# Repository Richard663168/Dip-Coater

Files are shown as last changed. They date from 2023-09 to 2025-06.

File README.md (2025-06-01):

# Dip-Coater
**Design of an Inexpensive, Microcontroller-based Dip Coater for Automated Thin Film Deposition**  

<p align="center">  
dipcoater  
  
**Animated Dip Coater Assembly Video**: https://youtu.be/RGj2P8bEvw4?si=eDrItM7gs5JFvn3  

Sections in this README:  

[1. Materials](#materials)

[2. 3D Printing Instructions](#3d-printing-instructions)

[3. Laser Cutting Instructions](#laser-cutting-instructions)  

[4. Circuit Design](#circuit-design)  

[5. Assembly Instructions](#assembly-instructions)  

[6. Using the Dip Coater](#using-the-dip-coater)  

## Materials  
Links provided below are only for reference.  

**Main Components**
| Item | Quantity | Reference Price | Source |
| ----------------------- | --------------- |---------------- |---------------- |
| [Arduino Mega 2560](https://www.amazon.com/ARDUINO-MEGA-2560-REV3-A000067/dp/B0046AMGW0)| 1  | $20.99 for 1|Amazon |
| ST7789 2.4” SPI LCD | 1  | $6.99 for 1| Taobao|
| [Nema 17 Stepper Motor](https://www.amazon.com/dp/B07THK76QQ/ref=twister_B07ZVLYL25?_encoding=UTF8&psc=1)  |1  | $10.99 for 1|Amazon|
| [2.1x5.5 12V Power Barrel](https://www.mcmaster.com/8320N117)  | 1 | $1.24 for 1|McMaster-Carr|
|[ DM542T Stepper Motor Driver  ](https://www.amazon.com/dp/B06Y5VPSFN?psc=1&ref=ppx_yo2ov_dt_b_product_details)| 1 | $28.99 for 1|Amazon|
| [DM320T Stepper Motor Driver](https://www.amazon.com/gp/product/B075R88FMN/ref=ppx_yo_dt_b_search_asin_title?ie=UTF8&psc=1)  |  1 | $15.99 for 1 |Amazon |
| [3x4 Matrix Keypad](https://www.adafruit.com/product/3845) |  1 | $6.50 for 1 |Adafruit Industries |
| [Screw Terminal Block Breakout Module for Arduino Mega](https://a.co/d/3ki64ex)  |  1 | $32.00 for 1 |Amazon |
| [FUYU FSL30 Mini Linear Stage Small Slide](https://a.co/d/0F66fWm)  |  1 | $118.00 for 1 |Amazon |
| [8-channel Bi-directional Logic Level Converter](https://www.adafruit.com/product/395?gclid=EAIaIQobChMIy_Wgl5aa-wIVg4zICh11Gg8HEAAYASAAEgIM5PD_BwE)|  1 | $7.95 for 1 |Adafruit Industries |
| [12V Push Button](https://www.amazon.com/gp/product/B08ZN73P2N/ref=ppx_yo_dt_b_search_asin_title?ie=UTF8&psc=1)  |  1 | $15.99 for 10 |Amazon |  
| [1 inch OD Steel Disk](https://a.co/d/e3l3wQv)  |  1 | $18.99 for 50 |Amazon |  
| [1/2 inch OD Steel Disk](https://a.co/d/1EjGdAq)  |  1 | $16.99 for 80 |Amazon |  
| [1 inch OD Neodymium magnet](https://www.mcmaster.com/7048T63)  |  1 | $8.57 for 1 |McMaster-Carr |  
| [1/2 inch OD Neodymium magnet](https://www.mcmaster.com/7048T56)  |  1 | $4.89 for 1 |McMaster-Carr |  

**Other Materials**
* 4 6mm 12" x 24" black acrylic sheets
* Wires
* Super glue
* 1 USB cable
* 1 2.1 x 5.5 12V power cable
* L-shape screw brackets
* Screws
* Clips
  
Black acrylic sheets could be replaced by other 6mm-thick laser cuttable materials.
## 3D Printing Instructions
3D printing files: Complete files are included in this current repository including .stl file format to be directly printable after slicing and .step file format to allow easy import and manipulation in most CAD software. All models were designed using Autodesk Fusion 360.

Designs are printed out using the Stratasys Elite and Stratasys Mojo with a layer height of 0.178mm (0.007in) and ABS plus P430 as the printing material.   

<details>

<summary>Printing Parts</summary>

* Beaker Disk
* Substrate Holder Connector
* Nema 17 Motor Holder
* Substrate Holder
* Disk Holder
* Tube Disk (Optional)
Asset 2@12x

</details>

## Laser Cutting Instructions
Laser Cutting files: Complete files are included in this current repository including .ai file format and .svg file format. All models were designed using Adobe Illustrator. Designs are laser cut using Epilog mini and Epilog Fusion with 6mm 12"x24" black acrylic sheets.  

The labels on the designs are for illustration only. It is recommanded to delete those labels before laser cutting or the labels might be engraved onto the final product. For Epilog laser cutters, the widths of the lines for laser cutting need to be set to 0.001pt and the area for engraving need to be filled black.

## Circuit Design

<p align="center">  
dipcoater_ciruit  
  
Breadboards shown in the circuit diagram are not required. It is recommanded to use solder or heat shrinking tubes to connect wires to electronic components and other wires in order to secure the connections.

## Assembly Instructions  
The **Complete Dip Coater** CAD file could be used as a reference on how to assemble the dip coater.  
1. Glue board **#3** and board **#2** onto board **#1**; Note that the back of the three pieces should not align: there is a 6mm distance between the back of board **#1** and the backs of both boards **#2** and **#3**
<p align="center">  
  

2. Use sandpaper or other sanding tools to make the edge of board **#4** fit the base and screw in the **ST7789 2.4” SPI LCD**, 2 **12V push buttons**, and the **3 x 4 keypad**
3. Glue board **#4** onto the dip coater
<p align="center">  


4.  Glue **Nema 17 Holder** onto the dip coater and place the **Nema 17 motor** inside
<p align="center">  


5. Glue boards **#5**, **#6**, and **#7** onto dip coater
<p align="center">  


6. Glue board **#8** onto the dip coater
<p align="center">  


7. Mount **FUYU FSL30 Mini Linear Stage Small Slide** onto board **#8** using screws
<p align="center">  


8. Connect all electronic components inside the dip coater based on the circuit diagram; USB cable and 2.1 x 5.5 power cable can come out through holes on board **#2**
9. Connect board **#9** to the dip coater using L-shape screw brackets, making future repairs and replacements easier
<p align="center">  


10. Connect board **#10** to the dip coater using L-shape screw brackets, making future repairs and replacements easier
<p align="center">  


11. Stick **1/2 inch OD Steel Disk** onto **Substrate Holder Connector** and **1/2 inch OD Neodymium Magnet** and a **clip** onto **Substrate Holder**
<p align="center">  


12. Stick **1 inch OD Steel Disk** onto **Disk Base** and **1 inch OD Neodymium Magnet** onto **Beaker Disk**
<p align="center">  


13. Attach **Substrate Holder Connector**, **Substrate Holder**, **Disk Base**, and **Beaker Disk** onto the dip coater; note that **Substrate Holder** and **Beaker Disk** can be removed or reattached anytime
<p align="center">  


14. Upload Arduino program provided in this repository to **Arduino Mega Microcontroller**
15. Download Processing and open **Dip_Coater_2_GUI** provided in this repository to start using the dip coater
## Using the Dip CoaterScreenshot 2025-05-30 at 8 23 23 PM

* Once the Processing file is opened, **Line 69 needs to be adjusted** based on the name of the PC's USB port before running the program.
* For each solution placed on the beaker disk, the user is able to choose the speed of which the substrate come out.
* The hold time (drying time) on top and the time that substrate is submerged in solution (time in solution) can be set.
* The number of solutions placed on the beaker disk can be set to 1, 2, or 3.
  * If the number of solutions is selected to be 1, the substrate will only go into solution 1 repeatly.
  * If the number of solutions is selected to be 2 or 3, the substrate will alternate among the selected solutions.
* How deep the substrate goes into the solutions can be adjusted using the Position slider
  * Negative numbers indicate milimiters higher than the default height and positive numbers indicate milimiters lower than the default height.
* The size of the substrate can be set using the Substrate Length text field.
* On the right side of the control panel, the user can save and load presets.
* Once all parameters are set and the **Start** button is clicked, the dip coater will start.
  * Estimated time until completion will be displayed on the bottom left corner of the GUI
* **12V push buttons** on the dip coater are for manual calibration of the linear actuator (They are rarely needed).  
* **3 x 4 keypad** is for manual calibration of the position of the beaker disk.
  * By inputing the desired rotating angle in degrees and hitting Enter, the beaker disk will rotate to the corresponding position.

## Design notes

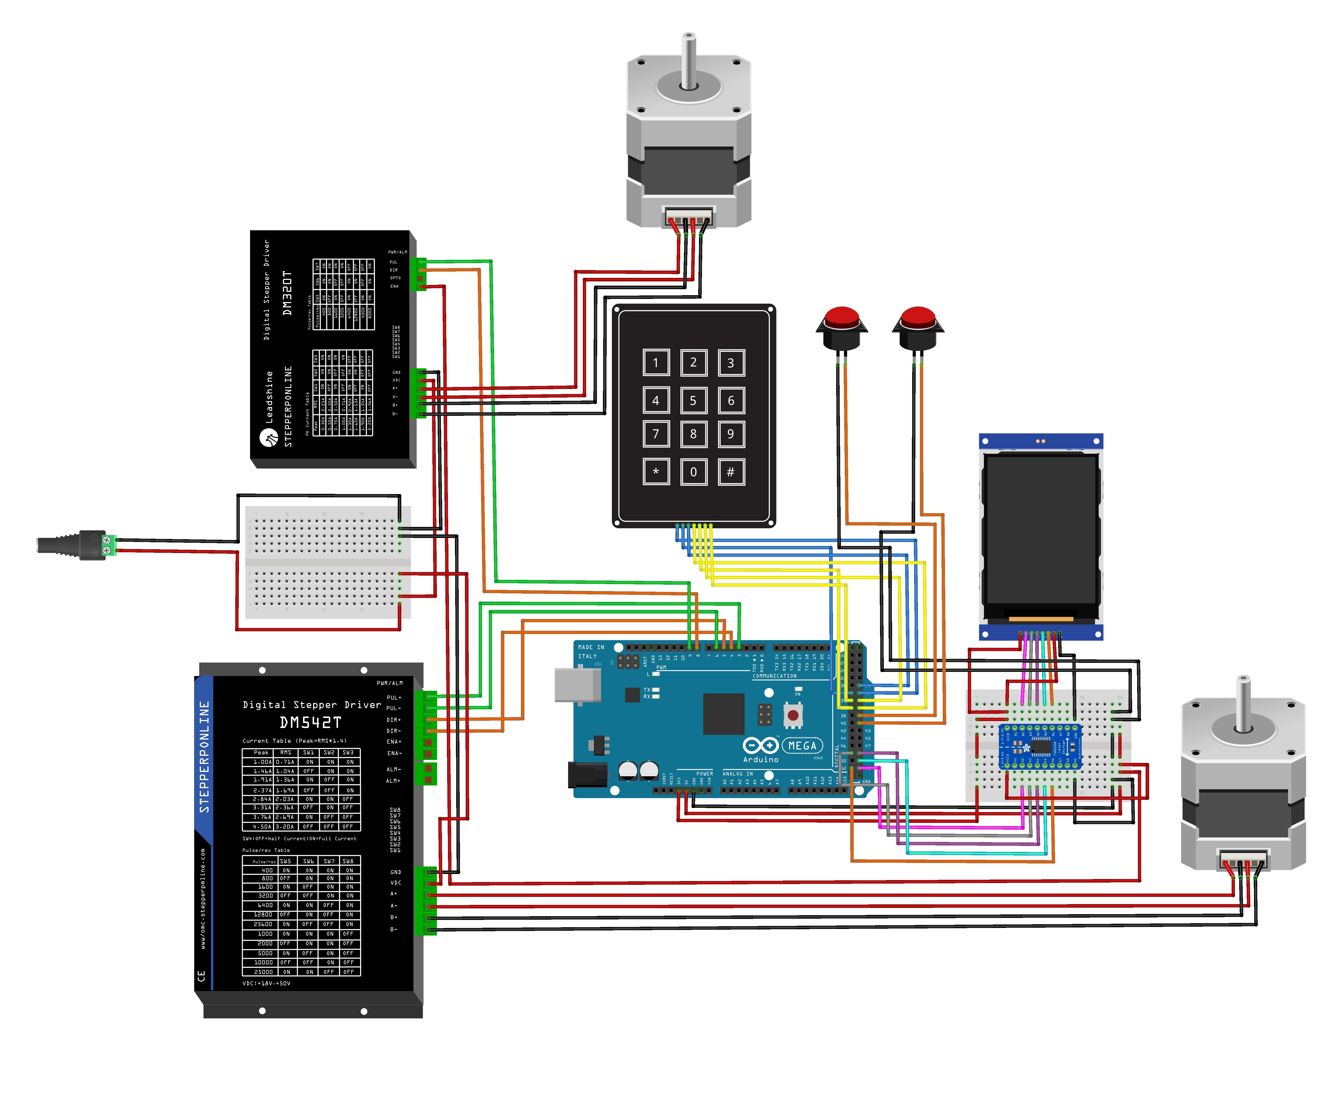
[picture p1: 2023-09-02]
Dip_Coater_Circuit Diagram.jpg

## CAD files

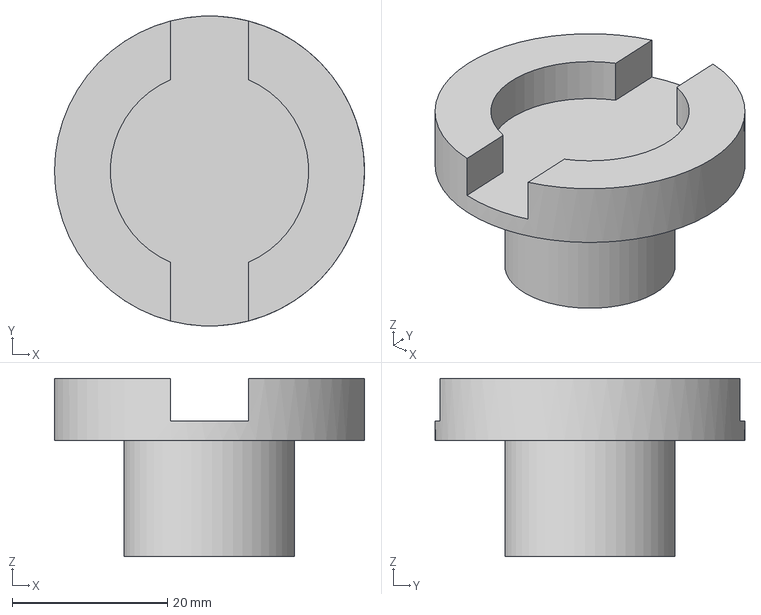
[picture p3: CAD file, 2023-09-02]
Dip_Coater_3D_Printing_Files/Disk Base.step
40.0 x 40.0 x 23.0 mm

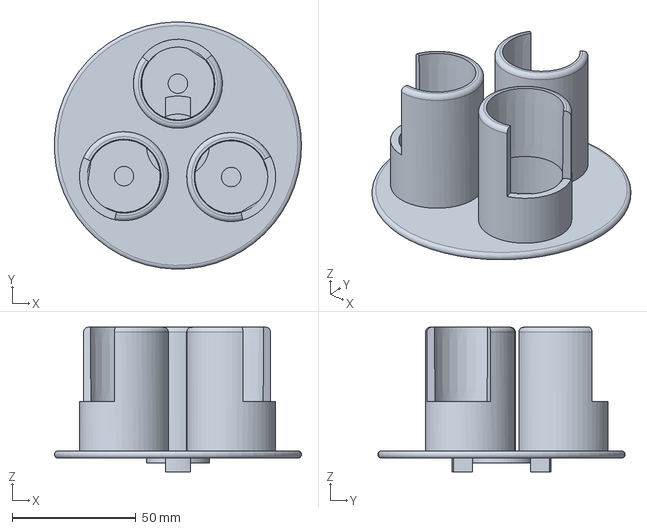
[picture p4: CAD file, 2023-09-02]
Dip_Coater_3D_Printing_Files/Disk with 3 Tube Holders.step
99.9 x 100.0 x 58.5 mm

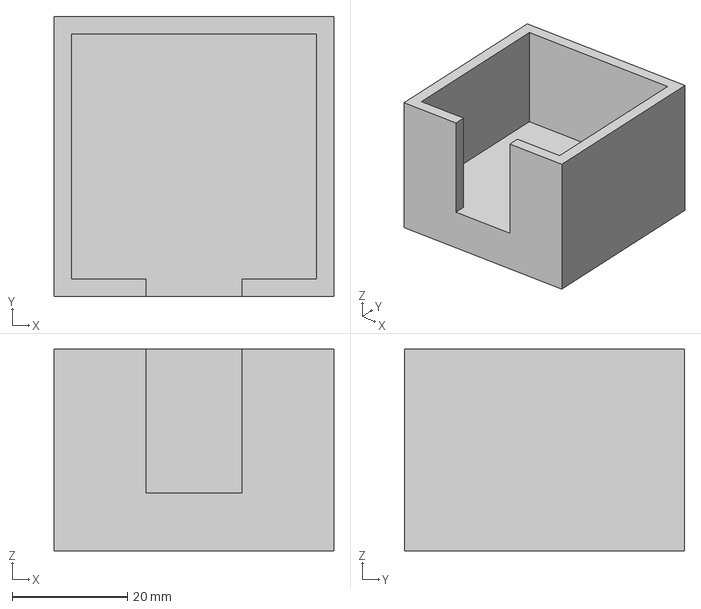
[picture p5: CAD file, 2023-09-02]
Dip_Coater_3D_Printing_Files/Nema 17 Holder.step
48.6 x 48.6 x 35.0 mm

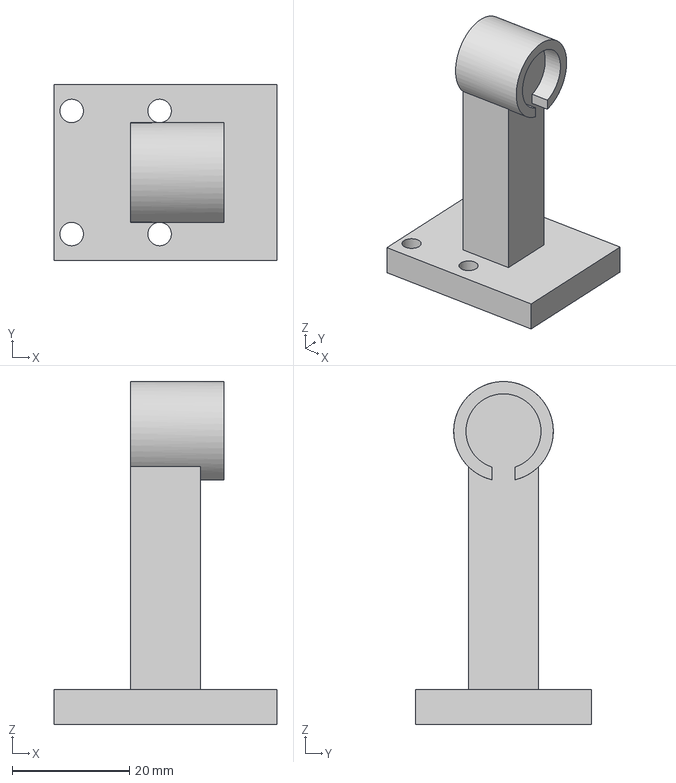
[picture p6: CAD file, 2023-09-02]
Dip_Coater_3D_Printing_Files/Substrate Holder Connector.step
38.0 x 30.0 x 58.5 mm

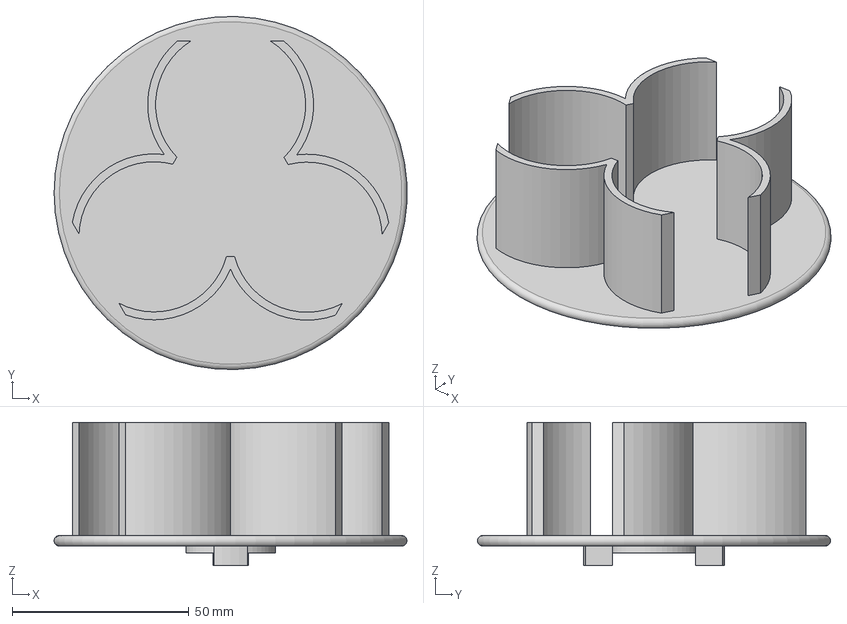
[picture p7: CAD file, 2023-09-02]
Dip_Coater_3D_Printing_Files/Beaker Disk.step
99.9 x 100.0 x 40.5 mm

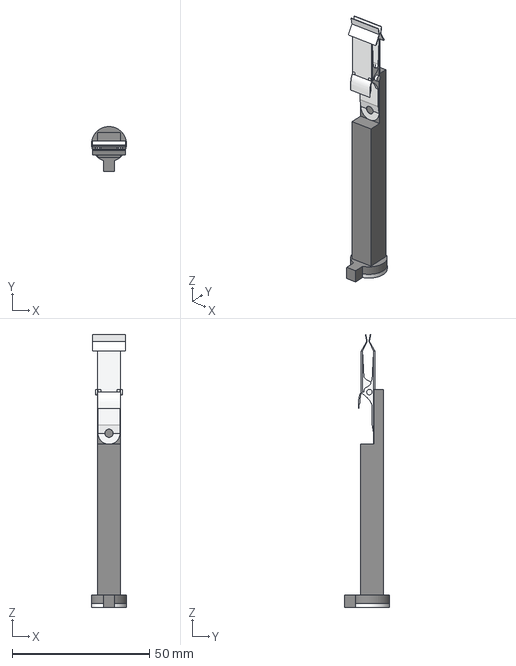
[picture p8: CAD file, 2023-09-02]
Dip_Coater_3D_Printing_Files/Substrate_Holder.step
12.7 x 16.4 x 99.5 mm

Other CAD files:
Dip_Coater_3D_Printing_Files/Beaker Disk.stl
Dip_Coater_3D_Printing_Files/Disk Base.stl
Dip_Coater_3D_Printing_Files/Disk with 3 Tube Holders.stl
Dip_Coater_3D_Printing_Files/Nema 17 Holder.stl
Dip_Coater_3D_Printing_Files/Substrate Holder Connector.stl
Dip_Coater_3D_Printing_Files/Substrate_Holder.stl

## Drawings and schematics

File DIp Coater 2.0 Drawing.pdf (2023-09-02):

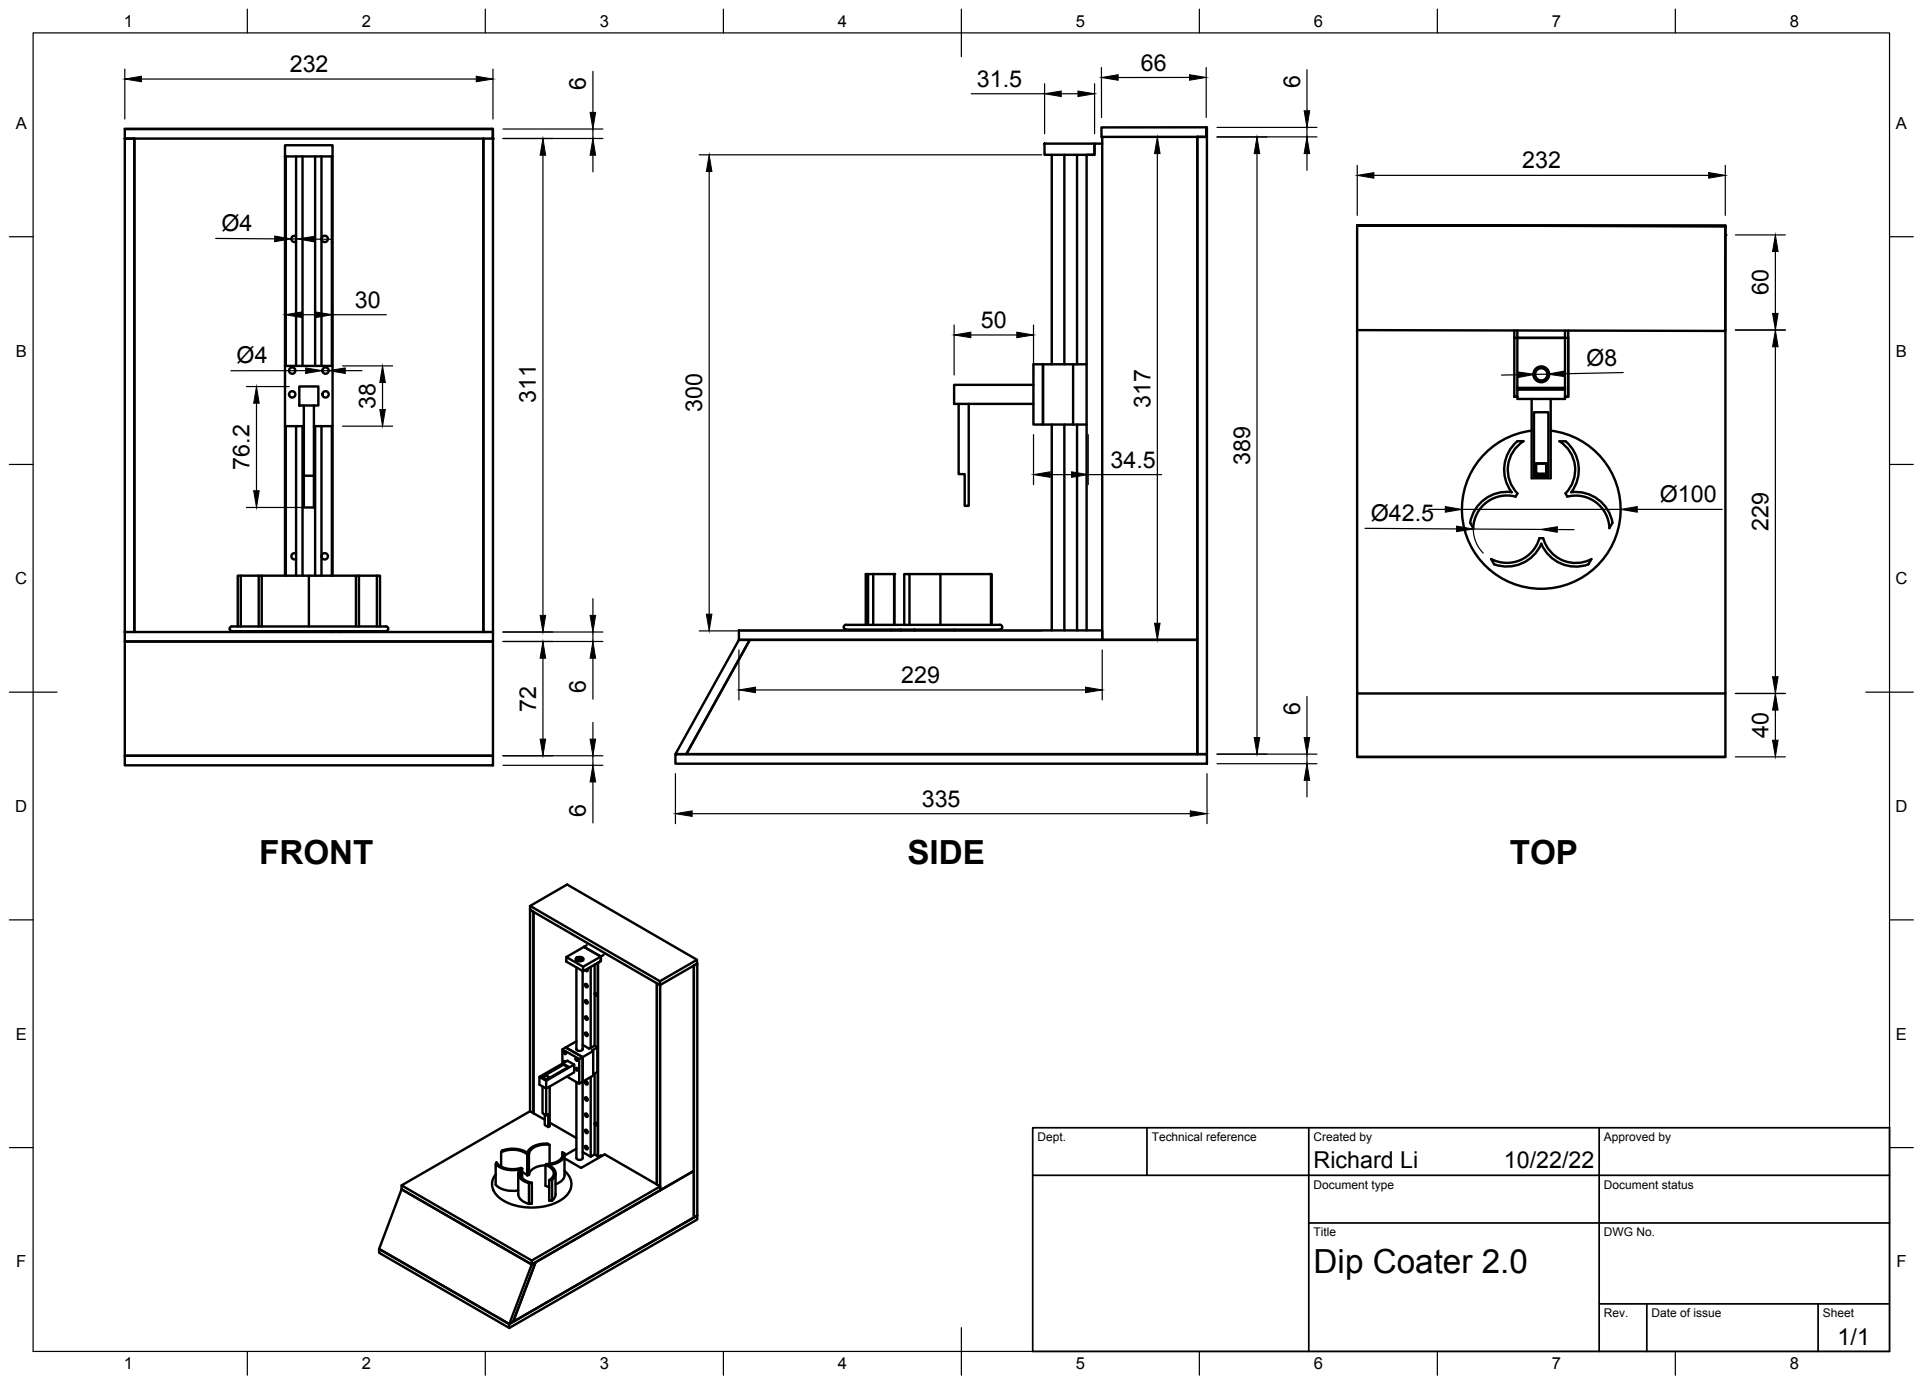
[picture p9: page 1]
Title; DWG No.; Rev.; Date of issue; Sheet; Dip Coater 2.0; Richard Li 311

Dept. | Technical reference | Created by 10/22/22 | Approved by

Document type | Document status

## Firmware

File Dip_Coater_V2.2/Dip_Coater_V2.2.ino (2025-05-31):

//include necessary libraries
#include <Adafruit_ST7789.h>
#include <gfxfont.h>
#include <Wire.h>
#include <Adafruit_GFX.h>
#include <Keypad.h>
#include <SPI.h>
#include <Stepper.h>
#include <Fonts/FreeSerif12pt7b.h>

//define 3x4 keypad
const byte ROWS = 4; //four rows
const byte COLS = 3; //three columns
char keys[ROWS][COLS] = {
  {'1','2','3'},
  {'4','5','6'},
  {'7','8','9'},
  {'*','0','#'},
};
byte rowPins[ROWS] = {34, 35, 36, 37}; //connect to the row pinouts of the keypad
byte colPins[COLS] = {31, 32, 33}; //connect to the column pinouts of the keypad
Keypad keypad = Keypad(makeKeymap(keys), rowPins, colPins, ROWS, COLS);

//define st7789 pins
#define TFT_MOSI 51  // SDA Pin on ESP32
#define TFT_SCLK 52  // SCL Pin on ESP32
#define TFT_CS   53  // Chip select control pin
#define TFT_DC   48  // Data Command control pin
#define TFT_RST  49  // Reset pin (could connect to RST pin)
Adafruit_ST7789 tft = Adafruit_ST7789(TFT_CS, TFT_DC, TFT_RST); 

//define colors for lcd display
#define BLACK    0x0000
#define BLUE     0x001F
#define RED      0xF800
#define GREEN    0x07E0
#define CYAN     0x07FF
#define MAGENTA  0xF81F
#define YELLOW   0xFFE0
#define WHITE    0xFFFF

//set pins for rotating platform motor
int in1 = 4;
int in2 = 5;
int in3 = 6;
int in4 = 3;

//set pins for vertical motor
int in5 = 8;
int in6 = 9;

// include files to run bitmap
#if defined(__AVR__)
    #include <avr/pgmspace.h>
#elif defined(__PIC32MX__)
    #define PROGMEM
#elif defined(__arm__)
    #define PROGMEM
#endif
const uint16_t LOGO[6083] PROGMEM={
    0xffff, 0xffff, 0xffff, 0xffff, 0xffff, 0xffff, 0xffff, 0xffff, 0xffff, 0xffff, 0xffff, 0xffff, 0xffff, 0xffff, 0xffff, 0xffff, 0xffff, 0xffff, 0xffff, 0xffff, 0xffff, 0xffff, 0xffff, 0xffff, 0xffff, 0xffff, 0xffff, 0xffff, 0xffff, 0xffff, 0xffff, 0x0000, 0x0000, 0x0000, 0x0000, 0x0000, 0x0000, 0x0000, 0x0000, 0x0000, 0x0000, 0x0000, 0x0000, 0x0000, 0x0000, 0x0000, 0xffff, 0xffff, 0xffff, 0xffff, 0xffff, 0xffff, 0xffff, 0xffff, 0xffff, 0xffff, 0xffff, 0xffff, 0xffff, 0xffff, 0xffff, 0xffff, 0xffff, 0xffff, 0xffff, 0xffff, 0xffff, 0xffff, 0xffff, 0xffff, 0xffff, 0xffff, 0xffff, 0xffff, 0xffff, 0xffff, 0xffff, 0xffff, 0xffff, 
    0xffff, 0xffff, 0xffff, 0xffff, 0xffff, 0xffff, 0xffff, 0xffff, 0xffff, 0xffff, 0xffff, 0xffff, 0xffff, 0xffff, 0xffff, 0xffff, 0xffff, 0xffff, 0xffff, 0xffff, 0xffff, 0xffff, 0xffff, 0xffff, 0xffff, 0xffff, 0xffff, 0xffff, 0x0000, 0x0000, 0x0000, 0x0000, 0x0000, 0x0000, 0x0000, 0x0000, 0x0000, 0x0000, 0x0000, 0x0000, 0x0000, 0x0000, 0x0000, 0x0000, 0x0000, 0x0000, 0x0000, 0x0000, 0x0000, 0x0000, 0xffff, 0xffff, 0xffff, 0xffff, 0xffff, 0xffff, 0xffff, 0xffff, 0xffff, 0xffff, 0xffff, 0xffff, 0xffff, 0xffff, 0xffff, 0xffff, 0xffff, 0xffff, 0xffff, 0xffff, 0xffff, 0xffff, 0xffff, 0xffff, 0xffff, 0xffff, 0xffff, 0xffff, 0xffff, 
    0xffff, 0xffff, 0xffff, 0xffff, 0xffff, 0xffff, 0xffff, 0xffff, 0xffff, 0xffff, 0xffff, 0xffff, 0xffff, 0xffff, 0xffff, 0xffff, 0xffff, 0xffff, 0xffff, 0xffff, 0xffff, 0xffff, 0xffff, 0xffff, 0xffff, 0x0000, 0x0000, 0x0000, 0x0000, 0x0000, 0x0000, 0x0000, 0x0000, 0x0000, 0x0000, 0x0000, 0x0000, 0x0000, 0x0000, 0x0000, 0x0000, 0x0000, 0x0000, 0x0000, 0x0000, 0x0000, 0x0000, 0x0000, 0x0000, 0x0000, 0x0000, 0x0000, 0xffff, 0xffff, 0xffff, 0xffff, 0xffff, 0xffff, 0xffff, 0xffff, 0xffff, 0xffff, 0xffff, 0xffff, 0xffff, 0xffff, 0xffff, 0xffff, 0xffff, 0xffff, 0xffff, 0xffff, 0xffff, 0xffff, 0xffff, 0xffff, 0xffff, 0xffff, 0xffff, 
    0xffff, 0xffff, 0xffff, 0xffff, 0xffff, 0xffff, 0xffff, 0xffff, 0xffff, 0xffff, 0xffff, 0xffff, 0xffff, 0xffff, 0xffff, 0xffff, 0xffff, 0xffff, 0xffff, 0xffff, 0xffff, 0xffff, 0xffff, 0x0000, 0x0000, 0x0000, 0x0000, 0x0000, 0x0000, 0x0000, 0x0000, 0x0000, 0x0000, 0x0000, 0x0000, 0x0000, 0x0000, 0x0000, 0x0000, 0x0000, 0x0000, 0x0000, 0x0000, 0x0000, 0x0000, 0x0000, 0x0000, 0x0000, 0x0000, 0x0000, 0x0000, 0x0000, 0x0000, 0x0000, 0xffff, 0xffff, 0xffff, 0xffff, 0xffff, 0xffff, 0xffff, 0xffff, 0xffff, 0xffff, 0xffff, 0xffff, 0xffff, 0xffff, 0xffff, 0xffff, 0xffff, 0xffff, 0xffff, 0xffff, 0xffff, 0xffff, 0xffff, 0xffff, 0xffff, 
    0xffff, 0xffff, 0xffff, 0xffff, 0xffff, 0xffff, 0xffff, 0xffff, 0xffff, 0xffff, 0xffff, 0xffff, 0xffff, 0xffff, 0xffff, 0xffff, 0xffff, 0xffff, 0xffff, 0xffff, 0xffff, 0x0000, 0x0000, 0x0000, 0x0000, 0x0000, 0x0000, 0x0000, 0x0000, 0x0000, 0x0000, 0x0000, 0x0000, 0x0000, 0x0000, 0x0000, 0x0000, 0x0000, 0x0000, 0x0000, 0x0000, 0x0000, 0x0000, 0x0000, 0x0000, 0x0000, 0x0000, 0x0000, 0x0000, 0x0000, 0x0000, 0x0000, 0x0000, 0x0000, 0x0000, 0x0000, 0xffff, 0xffff, 0xffff, 0xffff, 0xffff, 0xffff, 0xffff, 0xffff, 0xffff, 0xffff, 0xffff, 0xffff, 0xffff, 0xffff, 0xffff, 0xffff, 0xffff, 0xffff, 0xffff, 0xffff, 0xffff, 0xffff, 0xffff, 
    0xffff, 0xffff, 0xffff, 0xffff, 0xffff, 0xffff, 0xffff, 0xffff, 0xffff, 0xffff, 0xffff, 0xffff, 0xffff, 0xffff, 0xffff, 0xffff, 0xffff, 0xffff, 0xffff, 0xffff, 0x0000, 0x0000, 0x0000, 0x0000, 0x0000, 0x0000, 0x0000, 0x0000, 0x0000, 0x0000, 0x0000, 0x0000, 0x0000, 0x0000, 0x0000, 0x0000, 0x0000, 0x0000, 0x0000, 0x0000, 0x0000, 0x0000, 0x0000, 0x0000, 0x0000, 0x0000, 0x0000, 0x0000, 0x0000, 0x0000, 0x0000, 0x0000, 0x0000, 0x0000, 0x0000, 0x0000, 0x0000, 0xffff, 0xffff, 0xffff, 0xffff, 0xffff, 0xffff, 0xffff, 0xffff, 0xffff, 0xffff, 0xffff, 0xffff, 0xffff, 0xffff, 0xffff, 0xffff, 0xffff, 0xffff, 0xffff, 0xffff, 0xffff, 0xffff, 
    0xffff, 0xffff, 0xffff, 0xffff, 0xffff, 0xffff, 0xffff, 0xffff, 0xffff, 0xffff, 0xffff, 0xffff, 0xffff, 0xffff, 0xffff, 0xffff, 0xffff, 0xffff, 0xffff, 0x0000, 0x0000, 0x0000, 0x0000, 0x0000, 0x0000, 0x0000, 0x0000, 0x0000, 0x0000, 0x0000, 0x0000, 0x0000, 0xffff, 0xffff, 0xffff, 0xffff, 0xffff, 0xffff, 0xffff, 0xffff, 0xffff, 0xffff, 0xffff, 0xffff, 0xffff, 0x0000, 0x0000, 0x0000, 0x0000, 0x0000, 0x0000, 0x0000, 0x0000, 0x0000, 0x0000, 0x0000, 0x0000, 0x0000, 0x0000, 0xffff, 0xffff, 0xffff, 0xffff, 0xffff, 0xffff, 0xffff, 0xffff, 0xffff, 0xffff, 0xffff, 0xffff, 0xffff, 0xffff, 0xffff, 0xffff, 0xffff, 0xffff, 0xffff, 0xffff, 
    0xffff, 0xffff, 0xffff, 0xffff, 0xffff, 0xffff, 0xffff, 0xffff, 0xffff, 0xffff, 0xffff, 0xffff, 0xffff, 0xffff, 0xffff, 0xffff, 0xffff, 0x0000, 0x0000, 0x0000, 0x0000, 0x0000, 0x0000, 0x0000, 0x0000, 0x0000, 0x0000, 0x0000, 0x0000, 0xffff, 0xffff, 0xffff, 0xffff, 0xffff, 0xffff, 0xffff, 0xffff, 0xffff, 0xffff, 0xffff, 0xffff, 0xffff, 0xffff, 0xffff, 0xffff, 0xffff, 0xffff, 0xffff, 0x0000, 0x0000, 0x0000, 0x0000, 0x0000, 0x0000, 0x0000, 0x0000, 0x0000, 0x0000, 0x0000, 0x0000, 0xffff, 0xffff, 0xffff, 0xffff, 0xffff, 0xffff, 0xffff, 0xffff, 0xffff, 0xffff, 0xffff, 0xffff, 0xffff, 0xffff, 0xffff, 0xffff, 0xffff, 0xffff, 0xffff, 
    0xffff, 0xffff, 0xffff, 0xffff, 0xffff, 0xffff, 0xffff, 0xffff, 0xffff, 0xffff, 0xffff, 0xffff, 0xffff, 0xffff, 0xffff, 0xffff, 0x0000, 0x0000, 0x0000, 0x0000, 0x0000, 0x0000, 0x0000, 0x0000, 0x0000, 0x0000, 0x0000, 0xffff, 0xffff, 0xffff, 0xffff, 0xffff, 0xffff, 0xffff, 0xffff, 0xffff, 0xffff, 0xffff, 0xffff, 0xffff, 0xffff, 0xffff, 0xffff, 0xffff, 0xffff, 0xffff, 0xffff, 0xffff, 0xffff, 0xffff, 0x0000, 0x0000, 0x0000, 0x0000, 0x0000, 0x0000, 0x0000, 0x0000, 0x0000, 0x0000, 0x0000, 0xffff, 0xffff, 0xffff, 0xffff, 0xffff, 0xffff, 0xffff, 0xffff, 0xffff, 0xffff, 0xffff, 0xffff, 0xffff, 0xffff, 0xffff, 0xffff, 0xffff, 0xffff, 
    0xffff, 0xffff, 0xffff, 0xffff, 0xffff, 0xffff, 0xffff, 0xffff, 0xffff, 0xffff, 0xffff, 0xffff, 0xffff, 0xffff, 0xffff, 0x0000, 0x0000, 0x0000, 0x0000, 0x0000, 0x0000, 0x0000, 0x0000, 0x0000, 0x0000, 0xffff, 0xffff, 0xffff, 0xffff, 0xffff, 0xffff, 0xffff, 0xffff, 0xffff, 0xffff, 0xffff, 0xffff, 0xffff, 0xffff, 0xffff, 0xffff, 0xffff, 0xffff, 0xffff, 0xffff, 0xffff, 0xffff, 0xffff, 0xffff, 0xffff, 0xffff, 0xffff, 0x0000, 0x0000, 0x0000, 0x0000, 0x0000, 0x0000, 0x0000, 0x0000, 0x0000, 0x0000, 0xffff, 0xffff, 0xffff, 0xffff, 0xffff, 0xffff, 0xffff, 0xffff, 0xffff, 0xffff, 0xffff, 0xffff, 0xffff, 0xffff, 0xffff, 0xffff, 0xffff, 
    0xffff, 0xffff, 0xffff, 0xffff, 0xffff, 0xffff, 0xffff, 0xffff, 0xffff, 0xffff, 0xffff, 0xffff, 0xffff, 0xffff, 0x0000, 0x0000, 0x0000, 0x0000, 0x0000, 0x0000, 0x0000, 0x0000, 0x0000, 0x0000, 0xffff, 0xffff, 0xffff, 0xffff, 0xffff, 0xffff, 0xffff, 0xffff, 0xffff, 0xffff, 0xffff, 0xffff, 0xffff, 0xffff, 0xffff, 0xffff, 0xffff, 0xffff, 0xffff, 0xffff, 0xffff, 0xffff, 0xffff, 0xffff, 0xffff, 0xffff, 0xffff, 0xffff, 0xffff, 0x0000, 0x0000, 0x0000, 0x0000, 0x0000, 0x0000, 0x0000, 0x0000, 0x0000, 0x0000, 0xffff, 0xffff, 0xffff, 0xffff, 0xffff, 0xffff, 0xffff, 0xffff, 0xffff, 0xffff, 0xffff, 0xffff, 0xffff, 0xffff, 0xffff, 0xffff, 
    0xffff, 0xffff, 0xffff, 0xffff, 0xffff, 0xffff, 0xffff, 0xffff, 0xffff, 0xffff, 0xffff, 0xffff, 0xffff, 0xffff, 0x0000, 0x0000, 0x0000, 0x0000, 0x0000, 0x0000, 0x0000, 0x0000, 0xffff, 0xffff, 0xffff, 0xffff, 0xffff, 0xffff, 0xffff, 0xffff, 0xffff, 0xffff, 0xffff, 0xffff, 0xffff, 0xffff, 0xffff, 0xffff, 0xffff, 0xffff, 0xffff, 0xffff, 0xffff, 0xffff, 0xffff, 0xffff, 0xffff, 0xffff, 0xffff, 0xffff, 0xffff, 0xffff, 0xffff, 0xffff, 0xffff, 0x0000, 0x0000, 0x0000, 0x0000, 0x0000, 0x0000, 0x0000, 0x0000, 0x0000, 0xffff, 0xffff, 0xffff, 0xffff, 0xffff, 0xffff, 0xffff, 0xffff, 0xffff, 0xffff, 0xffff, 0xffff, 0xffff, 0xffff, 0xffff, 
    0xffff, 0xffff, 0xffff, 0xffff, 0xffff, 0xffff, 0xffff, 0xffff, 0xffff, 0xffff, 0xffff, 0xffff, 0xffff, 0x0000, 0x0000, 0x0000, 0x0000, 0x0000, 0x0000, 0x0000, 0x0000, 0xffff, 0xffff, 0xffff, 0xffff, 0xffff, 0xffff, 0xffff, 0xffff, 0xffff, 0xffff, 0xffff, 0xffff, 0xffff, 0xffff, 0xffff, 0xffff, 0xffff, 0xffff, 0xffff, 0xffff, 0xffff, 0xffff, 0xffff, 0xffff, 0xffff, 0xffff, 0xffff, 0xffff, 0xffff, 0xffff, 0xffff, 0xffff, 0xffff, 0xffff, 0xffff, 0x0000, 0x0000, 0x0000, 0x0000, 0x0000, 0x0000, 0x0000, 0x0000, 0x0000, 0xffff, 0xffff, 0xffff, 0xffff, 0xffff, 0xffff, 0xffff, 0xffff, 0xffff, 0xffff, 0xffff, 0xffff, 0xffff, 0xffff, 
    0xffff, 0xffff, 0xffff, 0xffff, 0xffff, 0xffff, 0xffff, 0xffff, 0xffff, 0xffff, 0xffff, 0xffff, 0x0000, 0x0000, 0x0000, 0x0000, 0x0000, 0x0000, 0x0000, 0x0000, 0xffff, 0xffff, 0xffff, 0xffff, 0xffff, 0xffff, 0xffff, 0xffff, 0xffff, 0xffff, 0xffff, 0xffff, 0xffff, 0xffff, 0xffff, 0xffff, 0xffff, 0xffff, 0xffff, 0xffff, 0xffff, 0xffff, 0xffff, 0xffff, 0xffff, 0xffff, 0xffff, 0xffff, 0xffff, 0xffff, 0xffff, 0xffff, 0xffff, 0xffff, 0xffff, 0xffff, 0xffff, 0x0000, 0x0000, 0x0000, 0x0000, 0x0000, 0x0000, 0x0000, 0x0000, 0xffff, 0xffff, 0xffff, 0xffff, 0xffff, 0xffff, 0xffff, 0xffff, 0xffff, 0xffff, 0xffff, 0xffff, 0xffff, 0xffff, 
    0xffff, 0xffff, 0xffff, 0xffff, 0xffff, 0xffff, 0xffff, 0xffff, 0xffff, 0xffff, 0xffff, 0x0000, 0x0000, 0x0000, 0x0000, 0x0000, 0x0000, 0x0000, 0x0000, 0xffff, 0xffff, 0xffff, 0xffff, 0xffff, 0xffff, 0xffff, 0xffff, 0xffff, 0xffff, 0xffff, 0xffff, 0xffff, 0xffff, 0xffff, 0xffff, 0xffff, 0xffff, 0xffff, 0xffff, 0xffff, 0xffff, 0xffff, 0xffff, 0xffff, 0xffff, 0xffff, 0xffff, 0xffff, 0xffff, 0xffff, 0xffff, 0xffff, 0xffff, 0xffff, 0xffff, 0xffff, 0xffff, 0xffff, 0x0000, 0x0000, 0x0000, 0x0000, 0x0000, 0x0000, 0x0000, 0x0000, 0xffff, 0xffff, 0xffff, 0xffff, 0xffff, 0xffff, 0xffff, 0xffff, 0xffff, 0xffff, 0xffff, 0xffff, 0xffff, 
    0xffff, 0xffff, 0xffff, 0xffff, 0xffff, 0xffff, 0xffff, 0xffff, 0xffff, 0xffff, 0xffff, 0x0000, 0x0000, 0x0000, 0x0000, 0x0000, 0x0000, 0x0000, 0xffff, 0xffff, 0xffff, 0xffff, 0xffff, 0xffff, 0xffff, 0xffff, 0xffff, 0xffff, 0xffff, 0xffff, 0xffff, 0xffff, 0xffff, 0xffff, 0xffff, 0xffff, 0xffff, 0xffff, 0xffff, 0xffff, 0xffff, 0xffff, 0xffff, 0xffff, 0xffff, 0xffff, 0xffff, 0xffff, 0xffff, 0xffff, 0xffff, 0xffff, 0xffff, 0xffff, 0xffff, 0xffff, 0xffff, 0xffff, 0xffff, 0x0000, 0x0000, 0x0000, 0x0000, 0x0000, 0x0000, 0x0000, 0xffff, 0xffff, 0xffff, 0xffff, 0xffff, 0xffff, 0xffff, 0xffff, 0xffff, 0xffff, 0xffff, 0xffff, 0xffff,
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
